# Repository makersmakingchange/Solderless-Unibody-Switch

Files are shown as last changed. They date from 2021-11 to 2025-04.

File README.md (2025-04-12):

# Solderless Unibody Switch
This repository contains design files and documentation for the Solderless Unibody Assitive Switch from Makers Making Change. 

MMC Library Listing: https://www.makersmakingchange.com/s/product/solderless-unibody-switch/01tJR000000699DYAQ

# Overview

The Solderless Unibody Switch is a simple switch that enables the user to easily activate a button. This device is suitable for users with limited dexterity and finger movement. The unique design of the single-piece print and few electronic components enables the maker to build the device without the use of a soldering iron, allowing the device to be more accessible and buildable for makers.

# Usage

The Solderless Unibody Switch is a simple device that is meant to be made accessible to makers that don’t have access to a soldering iron. This device is intended for individuals that are looking for a switch that has a lower profile.

An assembly guide can be found in the documentation on this device page. If you are fulfilling a request for this device, please take a look at the maker checklist document before you start the build to help walk you through the process.

# Build Instructions
An assembly guide can be found in the documentation on this device page. If you are fulfilling a request for this device, please take a look at the maker checklist document before you start the build to help walk you through the process.

# SKILLS REQUIRED

Fine motor skills – Applying a small amount of super glue
Pulling – Tightening zip tie
Gripping – Using tools/lighter

# TOOLS

Super glue
Flush cutters
Wire strippers
Heat Gun / Lighter
Needle nose pliers (optional)

# COMPONENTS

2x – 24-26ga. wire crimp connectors

1x – 3.5 mm mono cable

1x – 12 mm Tactile Switch

1x – 18 inch zip tie

# 3D PRINTING

1x – Body of switch (STL and printing guide can be found in the design files link above)

# Attribution

Justin Pezzin - Makers Making Change

<!-- ABOUT MMC START -->
## About Makers Making Change
[Makers Making Change Logo](https://www.makersmakingchange.com/)

Makers Making Change is a program of [Neil Squire](https://www.neilsquire.ca/), a Canadian non-profit that uses technology, knowledge, and passion to empower people with disabilities.

Makers Making Change leverages the capacity of community based Makers, Disability Professionals and Volunteers to develop and deliver affordable Open Source Assistive Technologies.

 - Website: [www.MakersMakingChange.com](https://www.makersmakingchange.com/)
 - GitHub: [makersmakingchange](https://github.com/makersmakingchange)
 - Bluesky: [@makersmakingchange.bsky.social](https://bsky.app/profile/makersmakingchange.bsky.social)
 - Instagram: [@makersmakingchange](https://www.instagram.com/makersmakingchange)
 - Facebook: [makersmakechange](https://www.facebook.com/makersmakechange)
 - LinkedIn: [Neil Squire Society](https://www.linkedin.com/company/neil-squire-society/)
 - Thingiverse: [makersmakingchange](https://www.thingiverse.com/makersmakingchange/about)
 - Printables: [MakersMakingChange](https://www.printables.com/@MakersMakingChange)

### Contact Us
For technical questions, to get involved, or to share your experience we encourage you to [visit our website](https://www.makersmakingchange.com/) or [contact us](https://www.makersmakingchange.com/s/contact).
<!-- ABOUT MMC END -->

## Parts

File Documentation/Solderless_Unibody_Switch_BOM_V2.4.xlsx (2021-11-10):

Device: Solderless Unibody Switch |  | Total Cost | Total Print time (hr) | Total filament (g)
Version: V2.4 | Date Created: 10/20/2021 | $6.03 | 0.42 | 7.4
Commercial Parts:
Part type (Electrical, Mechanical, Sanitization, etc.) | Part Name | Quantity Needed | Pkg Quantity | Price per package | Price per Unit | Price for qty needed | Link
Electrical | 3.5 mm mono cable | 1 | 1 | $4.40 | $4.40 | $4.40 | https://www.digikey.ca/short/pt54w9
Electrical | 12 mm Tactile Switch | 1 | 1 | $0.95 | $0.95 | $0.95 | https://www.digikey.ca/short/jvzq2d
Mechanical | 24-26ga. wire crimp connectors | 2 | 100 | $14.99 | $0.15 | $0.30 | https://www.amazon.ca/dp/B09CMP6VNK
Other | 18 inch zip tie | 1 | 50 | $9.99 | $0.20 | $0.20 | https://www.amazon.ca/Cable-Multi-Function-Nylon-Self-Locking-Ties%EF%BC%8C50/dp/B08B53VK69?hvadid=267679675369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
3D Printed Parts ESTIMATED PRICING USING 1KG ROLL COST: | $25.00
Part | Description | Quantity Needed | TOTAL Mass (g) | Estimated Price | Print Time (min) | Link
3D Printed Switch Body |  | 1 | 7.4 | $0.18 | 25
 |  |  |  | $0.00
 |  |  |  | $0.00
 |  |  |  | $0.00
 |  |  |  | $0.00
 |  |  | Total Print Cost: | $0.18
Tools for Assembly
Super glue
Flush cutters
Wire strippers
Heat Gun / Lighter
Needle nose pliers (optional)
Alternatives (if there are other sources for some parts link them below)
Part and description | Link
3.5 mm mono cable | https://www.allelectronics.com/item/cb-3510/10-cable-w/3.5-mm-mono-plug-both-ends/1.html
 | Local dollar store
24-26ga. wire crimp connectors | https://www.amazon.ca/26-24AWG-Insulated-Electrical-Terminal-Connector/dp/B07Y6KN83R?s=electronics

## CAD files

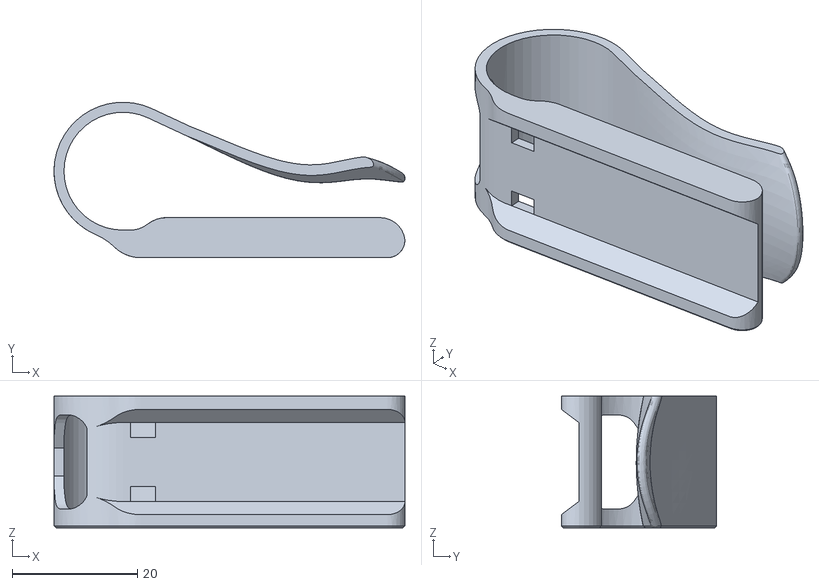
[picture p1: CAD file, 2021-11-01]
3D Print Files/Solderless unibody switch v2.4.stl
56.0 x 24.8 x 21.0

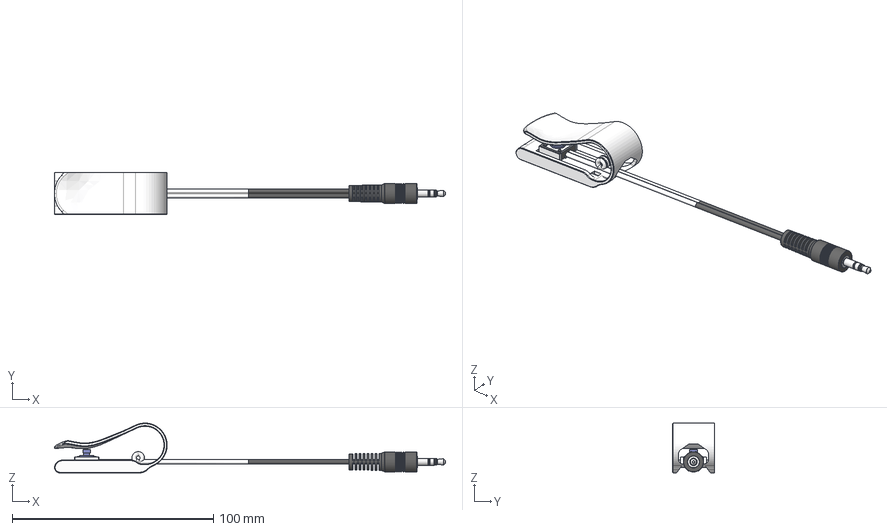
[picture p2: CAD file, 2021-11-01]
Design Files/SUS modified for drawing v6.step
194.4 x 21.0 x 24.8 mm
OMRON_B3F_5050 v3
plug

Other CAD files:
Design Files/SUS modified for drawing v6.f3z

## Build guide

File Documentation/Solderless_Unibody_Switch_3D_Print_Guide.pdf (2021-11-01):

V2.4 | October 2021

## Solderless Unibody Switch

## 3D PRINTING GUIDE

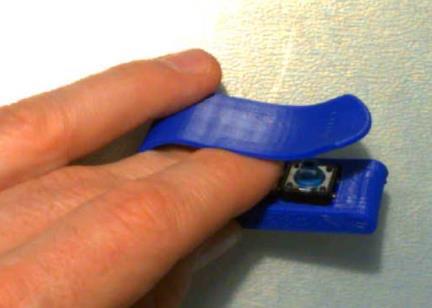
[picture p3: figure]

© 2021 by <Author>.

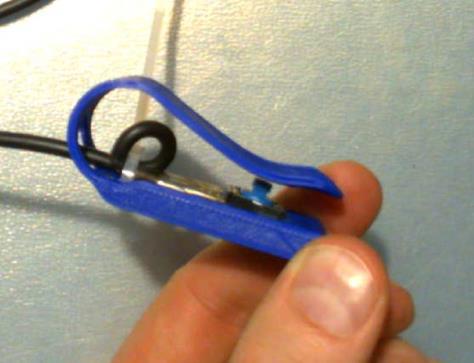
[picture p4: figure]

This work is licensed under the CC BY SA 4.0 License: http://creativecommons.org/licenses/by-sa/4.0
Files available at <Replace with MMC Library Link> | Page 1 of 1

### 3D Printing Summary

Metrics | Chamfered Edge down
Total Print Time (min) | 25
Total Number of Components | 1
Typical Total Mass (g) | 7.4g

### 3D Printing Settings

Print File Name | Qty | Total Print Time (hr:min) | Mass (g) | Infill (%) | Support (Y/N) | Layer Height/ Nozzle Diameter (mm) | Notes (orientation, special settings, etc)
Solderless_ Unibody_ Switch.stl | 1 | 0:25 | 7.4 | 100 | N | 0.3/0.4 | - Print in orientation given in STL - PLA, PETG, or ABS - Optional: brim

### Post-Processing

- Optional: removing brim

### Customization Options

- The Solderless Unibody Switch can be printed in any colour of filament

### Examples of Quality Prints:

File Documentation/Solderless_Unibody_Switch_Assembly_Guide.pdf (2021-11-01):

## Solderless Unibody Switch Assembly Guide

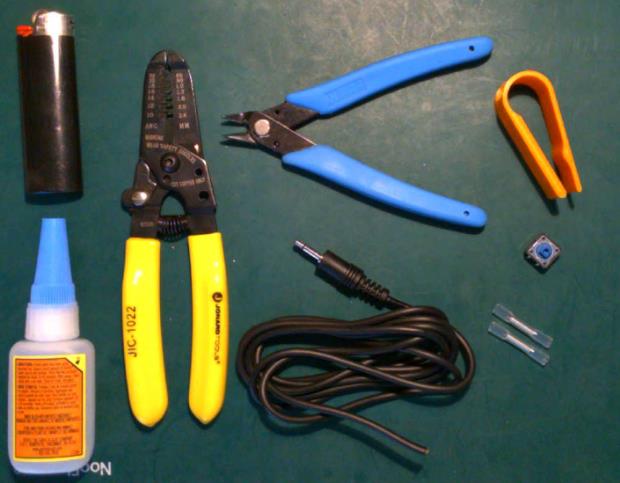
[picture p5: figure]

Tools:
- Super glue
- Flush cutters
- Wire strippers
- Needle nose pliers (optional)
- Heat Gun / Lighter

Parts:

Qty | Description | Link
2 | 24-26ga. wire crimp connectors | Amazon.ca (https://www.amazon.ca/dp/B09G6D9MV6)
1 | 18 inch zip tie | Amazon.ca (https://www.amazon.ca/Cable-Multi-Function-Nylon-Self-Locking-Ties%EF%BC%8C50/dp/B08B53VK69?hvadid=267679675369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)
1 | 3.5 mm mono cable • May be able to find these at local dollar store | All Electronics Corp (https://www.allelectronics.com/item/cb-3510/10-cable-w/3.5-mm-mono-plug-both-ends/1.html) Digikey (https://www.digikey.ca/short/pt54w9)
1 | 12 mm Tactile Switch | Digikey (https://www.digikey.ca/short/jvzq2d)
1 | 3D Printed Switch Body

Assembly Instructions:

Step | Image | Instruction

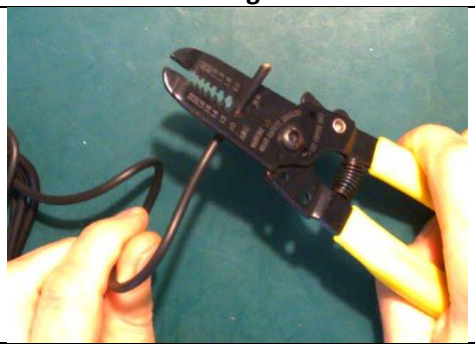
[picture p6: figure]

1 | | Remove one of the ends and strip the outer wire casing from the monocable. Expose about 2 cm of the internal wires.

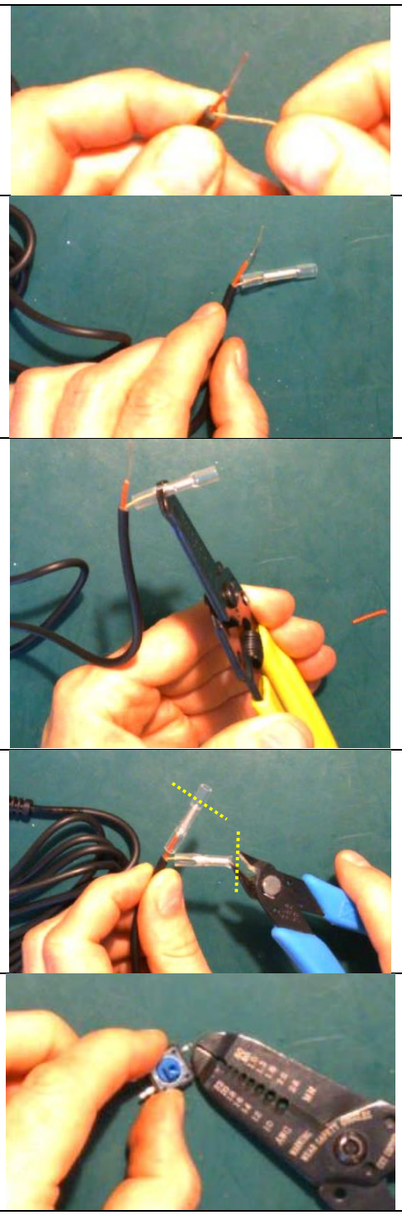
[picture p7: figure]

2 | Remove the casing from the inner wire(s) and tightly twist the braided copper ends.
3 | Test fit the crimp, and cut bare wire ends to length to leave limited wire exposed.
4 | Using the plier nose of the wire strippers, squeeze the crimp firmly to fix the wire. Can also use Needle Nose plier for this step.
5 | Trim the heat shrink from the open end of the crimp. It doesn’t need to be perfectly flush.
6 | Flatten both sets of leads on the Tactile Switch using the nose of the wire strippers.

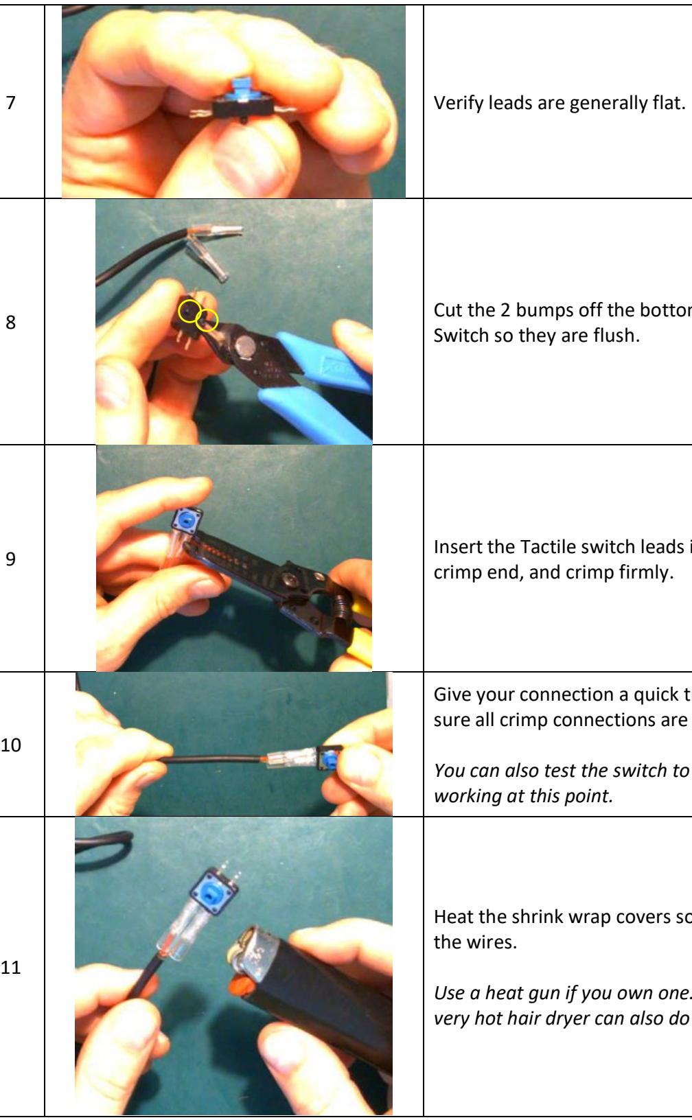
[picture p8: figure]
Verify leads are generally flat.

8 | Cut the 2 bumps off the bottom of the Tactile Switch so they are flush.
9 | Insert the Tactile switch leads into the open crimp end, and crimp firmly.
10 | Give your connection a quick tug test to make sure all crimp connections are secure. You can also test the switch to make sure it’s working at this point.
11 | Heat the shrink wrap covers so they reduce over the wires. Use a heat gun if you own one. If not, a lighter or very hot hair dryer can also do the job.

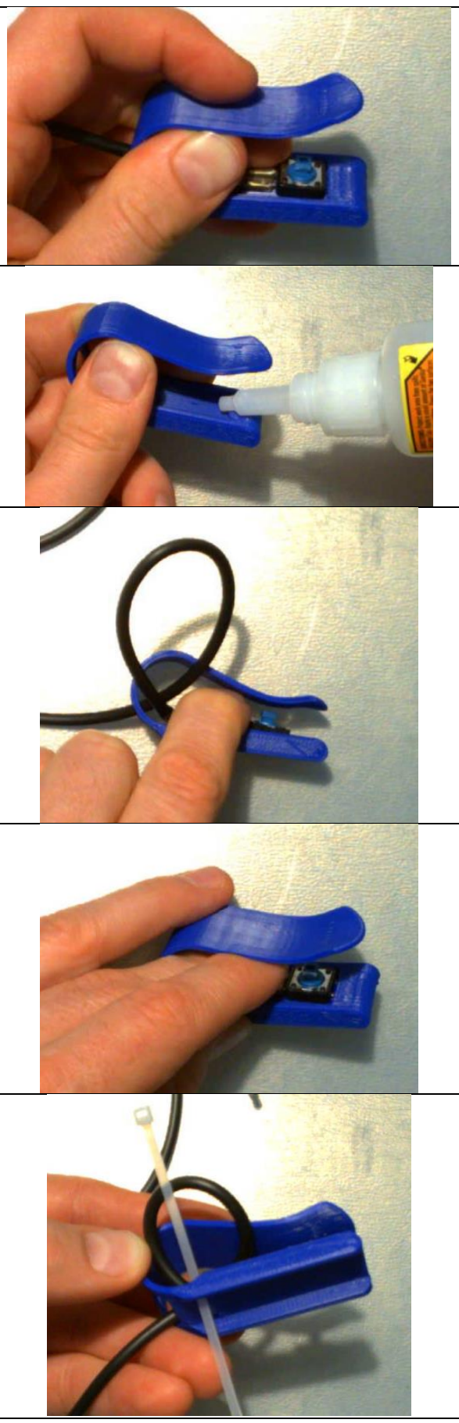
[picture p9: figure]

12 | Slide the Tactile Switch through the opening at the back of the switch body and insert the prongs under the lip at the front of the switch body. This is a test fit only. Making sure the prongs are slightly pointed down can help them insert easier.
13 | Work quickly here, but don’t rush. Add a good size drop of super glue in where the switch will sit.
14 | Slide the Tactile Switch through the opening at the back of the switch with enough extra wire to make a large loop.
15 | Re-insert the switch with the prongs under the lip. Hold it tight for 10 seconds until the glue sets. Warning: Careful not to glue your fingers!
16 | Insert a small tie strap, downward through one of the holes.

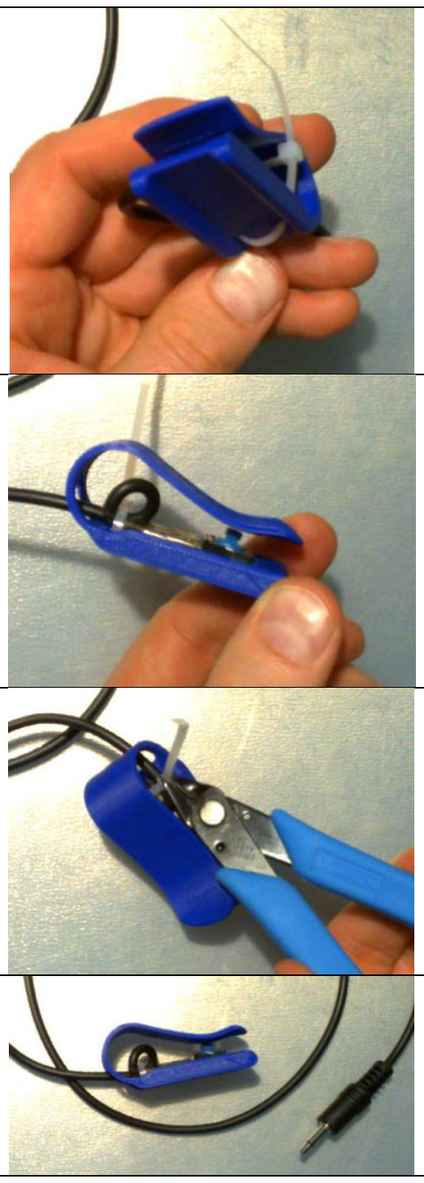
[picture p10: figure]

17 | Loop the tie strap back up and through the other slot.
18 | Making sure the tie strap passes through the middle of the wire loop connect the tie strap and pull it snug, but loose enough so the wire still moves easily. Then pull the wire out to reduce the size of the loop so it fits easily inside the switch body.
19 | Tighten the tie strap fully so the wire doesn’t move, then snip off the excess.
19 | Test your switch and then sit back and admire your handiwork. Great Work!!

Tip for Users:

- When setting this up for a user, adhesive Velcro or tie straps can help you mount it securely to a surface or round tube for reliable operation

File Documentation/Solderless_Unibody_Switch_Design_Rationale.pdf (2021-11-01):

V2.4 | October 2021

## Solderless Unibody Switch

## DESIGN RATIONALE

© 2021 by <Author>.
This work is licensed under the CC BY SA 4.0 License: http://creativecommons.org/licenses/by-sa/4.0
Files available at <Replace with MMC Library Link> | Page 1 of 3

### Introduction

The Solderless Unibody Switch is a simple switch that enables the user to easily activate a button. This device is suitable for users with limited dexterity and finger movement. The unique design of the single-piece print and few electronic components enables the maker to build the device without the use of a soldering iron, allowing the device to be more accessible and buildable for makers.

### Requirements

Must:
- The assembly of the device must be possible without a soldering iron
- The device components must be affordable and easily accessible
- 3D printed unibody design must be able to flex enough to press the switch button
- The 3D printed unibody design must be able to be printed in one piece

Should:
- The 3D printed unibody design should not require support material

### Ideation

Crimping: To see if crimps would be able to make a reliable switch connection without the use of a Crimp Tool, or heat gun (i.e., no specialized tooling).

3D Printed Unibody Design: Experimentation with 3D printed unibody design to see if the idea was feasible.

### Prototyping

Crimping:
- This demonstrates that the base plates for both the Light Touch & Raindrop can be easily modified for use with this crimped approach
- Found assembling each of the crimps onto the wire first much easier to manage compared to starting with them on the switch
- Important to ensure the crimps are supported and contained within the body of the switch to ensure the longest service life possible
- Crimps provide a very solid element to use a tie strap with, so also gives a pretty solid, and clean looking wire retention method

3D Printed Unibody Design:
- Removes the pain point of needing to find a hinge, or print small hinge parts

## DESIGN RATIONALE

Files available at <Replace with MMC Library Link> | Page 2 of 3
- Remains fairly low force, and design can be tweaked to reduce baseline forces from the body if needed
- Added super glue between the switch component and the 3D Printed body as an added control/retainment
- The legs on the opposite side of the switch are also mechanically retained under a small lip at the front of the base plate for additional control/retainment
- Limited stroke length, and low strain on the body
- Adding a curl upwards on the top end portion of the 3D printed switch body would allow for easier more reliable pressure to be applied to the switch inside

### Testing

- Printed in both PLA and PETG, which both worked
- If the switch slides from under your finger when you push the button, which it was found to stay in place
- Looping the cable where the twist tie is helping to reduce the strain on the crimp if the cord is pulled or twisted with daily use
- If the twist tie wrapping under the switch destabilized the device and caused it to rock side to side
- A larger circular surface area
- A small chamfer around the edge in contact with the print bed to reduce elephant foot
- Sharp corners on the front edge could be reduced or even chamfered to help break the edge
- An opportunity to reduce the height of the front edge so a user doesn’t have to lift their finger as far

## DESIGN RATIONALE

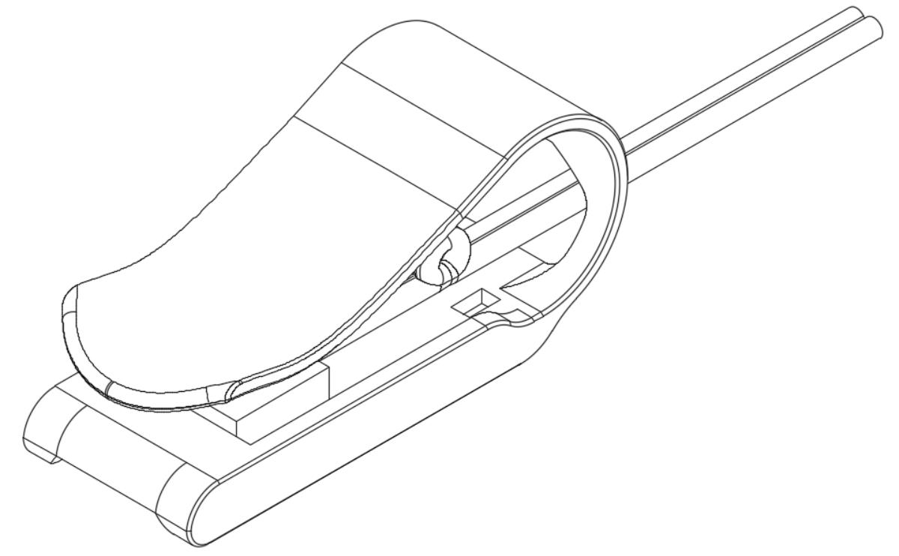
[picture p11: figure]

Files available at <Replace with MMC Library Link> | Page 3 of 3

### Final Design

### Opportunities for Improvement

- Could consider a two-part option to separate out the activation surface (more print orientation options, different colors, etc.)

### Credited Resources Used in Development

Makers Making Change. (October, 2021). Solderless Unibody Switch. https://makersmakingchange.com/forum/topic/solderless-unibody-switch/

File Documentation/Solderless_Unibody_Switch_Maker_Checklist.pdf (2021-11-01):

V2.4 | October 2021

# Solderless Unibody Switch

# MAKER CHECKLIST

© 2021 by <Author>.
This work is licensed under the CC BY SA 4.0 License: http://creativecommons.org/licenses/by-sa/4.0
Files available at <Replace with MMC Library Link> | Page 1 of 1

# Maker To Do List

## Ask user preferences (e.g., colour, any special requests, etc.) Order hardware components Gather tools and equipment 3D print file Assemble device

# Items to Give to User

## Device

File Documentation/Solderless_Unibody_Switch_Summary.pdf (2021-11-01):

V2.4 | October 2021

## Solderless Unibody Switch

## SUMMARY

© 2021 by <Author>.
This work is licensed under the CC BY SA 4.0 License: http://creativecommons.org/licenses/by-sa/4.0
Files available at <Replace with MMC Library Link> | Page 1 of 2

### Title

Solderless Unibody Switch

### Subtitle

Low-Force Assistive Switch

### Overview

The Solderless Unibody Switch is a simple switch that enables the user to easily activate a button. This device is suitable for users with limited dexterity and finger movement. The unique design of the singlepiece print and few electronic components enables the maker to build the device without the use of a soldering iron, allowing the device to be more accessible and buildable for makers.

### Usage

The Solderless Unibody Switch is a simple device that is meant to be made accessible to makers that don’t have access to a soldering iron.

### Cost

~$6 CA

### Build Instructions

SKILLS REQUIRED
Fine motor skills – Applying a small amount of super glue Pulling – Tightening zip tie
Gripping – Using tools and using a lighter

TIME REQUIRED
Print – 25 min
Device assembly – 20 min

TOOLS
Super glue
Flush cutters
Wire strippers
Heat Gun / Lighter
Needle nose pliers (optional)

V2.4 | October 2021

## Solderless Unibody Switch

## SUMMARY

© 2021 by <Author>.
This work is licensed under the CC BY SA 4.0 License: http://creativecommons.org/licenses/by-sa/4.0
Files available at <Replace with MMC Library Link> | Page 2 of 2

COMPONENTS
2x – 24-26ga. wire crimp connectors 1x – 3.5 mm mono cable
1x – 12 mm Tactile Switch

1x – 18 inch zip tie

3D PRINTING
1x – Solderless_Unibody_Switch.stl

## Attribution

Makers Making Change

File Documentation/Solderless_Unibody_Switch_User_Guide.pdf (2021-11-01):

V2.4 | October 2021

## Solderless Unibody Switch

## USER QUICK GUIDE

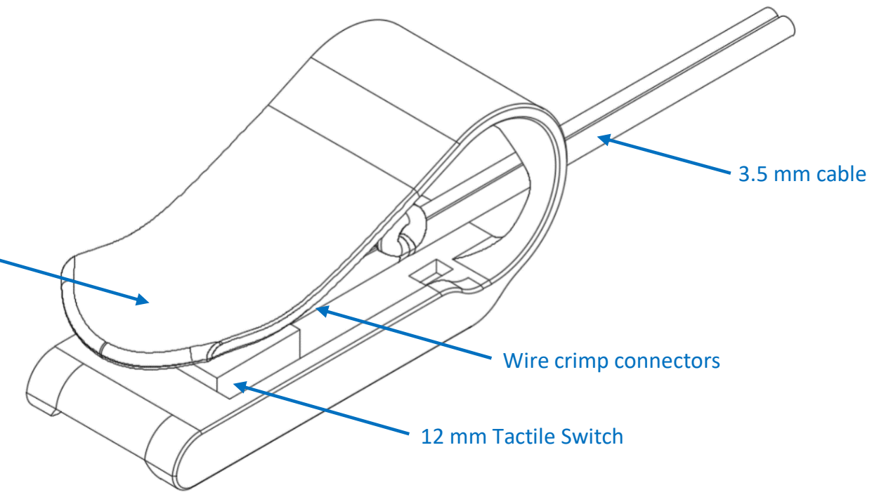
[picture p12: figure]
3.5 mm cable; Wire crimp connectors; 12 mm Tactile Switch

© 2021 by <Author>. This work is licensed under the CC BY SA 4.0 License: http://creativecommons.org/licenses/by-sa/4.0
Files available at <Replace with MMC Library Link> | Page 1 of 2

### Introduction

The Solderless Unibody Switch is a simple switch that enables the user to easily activate a button. This device is suitable for users with limited dexterity and finger movement. The unique design of the singlepiece print and few electronic components enables the maker to build the device without the use of a soldering iron, allowing the device to be more accessible and buildable for makers.

### Features

### Usage

Connect the 3.5 mm cable from the Solderless Unibody Switch to the assistive device and press the indented section to activate the switch.

### Compatibility

The Solderless Unibody Switch’s 3.5 mm male connector is compatible with a 3.5 mm female jack, found on most assistive technology devices.

### Specifications

Specification | Detail
Size | 56x21x25mm
Weight | 7.4g

Indented
section

V2.4 | October 2021

## Solderless Unibody Switch

## USER QUICK GUIDE

© 2021 by <Author>. This work is licensed under the CC BY SA 4.0 License: http://creativecommons.org/licenses/by-sa/4.0
Files available at <Replace with MMC Library Link> | Page 2 of 2

### Cleaning

The 3D printed body of the switch can be wiped clean with a paper towel or soft cloth, using a mild household detergent solution. Non-toxic biodegradable all-purpose cleaners are preferred. Do not use abrasive cleaners, as they will scratch the surface of the unit. Do not submerge the unit in any liquid, as it will damage the electronic components. If disinfection is required, Isopropyl alcohol may be applied with a wipe.

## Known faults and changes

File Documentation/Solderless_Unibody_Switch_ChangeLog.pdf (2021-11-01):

V2.4 | October 2021

## Solderless Unibody Switch

## CHANGELOG

© 2021 by <Author>. This work is licensed under the CC BY SA 4.0 License: http://creativecommons.org/licenses/by-sa/4.0
Files available at <Replace with MMC Library Link> | Page 1 of 1

## Version 1.0 | Date 8/12/2021

- Device is designed and test printed
- Device is assembled and tested
- Device files and instructions are posted on the forum for feedback

## Version 2.4 | Date 10/6/2021

- Bottom section of 3D printed body is sunk in to prevent the zip tie from impacting the stability of the device when on a table
- Top section of device is redesigned from a slope to a swooping design for a more ergonomic interaction when using the device with a finger and to prevent the device from sliding away from the user
